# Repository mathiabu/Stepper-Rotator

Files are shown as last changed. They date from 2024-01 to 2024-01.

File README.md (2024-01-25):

# Stepper-Rotator
Rotation machine for recirculating Organ-on-Chip systems. There are currently 2 versions of the machine: (A) with manual tilt adjustment and (B) with servo-motor controlled tilt adjust. As seen in the image of the fully mounted device, it consists of a main body and a changeable rotor that holds the chips. 

Usage instructions (Version A):
1. Mount the rotor and place the plates/chips.
2. Set the desired tilt by loosening, moving, and tightening the wing nuts on the side.
3. Connect the machine to the power supply (9-12 V) and turn it on (at the backside).
4. While the motor is off (after startup) you can adjust the speed between 0 and 2.5 rpm and also change the rotation direction (clockwise (CW) or counterclockwise (CCW)) by turning the knob.
5. To run the motor, press the on/off button. The user input is blocked while the motor is running. If you want to change the speed, turn the motor off, adjust the speed, and run it again.

Mounting instructions of the body (Version A). Please check the attached images if you are unsure how to mount the parts:
1. Laser-cut DXF files into acrylic. Use the following thickness for the different parts: Back, Front, Bottom, and Side: 5 mm, Top: 1.5 mm, Adapter: 6 mm. Use 2x Adapter-left and 2x Side-A. Delete the text and angle scale in Side-A and engrave this in the second step.
2. The sides contain a laser-engravement to display the tilt and on the backside a countersink for the power jack can be engraved. You have to align the engravement with the cut parts and create an overlay to only remove the difference in the software of your lasercutter. All engravements should be 1-2 mm deep.
3. 3D-print the STL files in a hard material using a FDM- or DLP-based printer. Use enough infill to be able to tap a thread later on. Print the mounting cubes 4x each (normal and mirrowed) and the front bar only 1x.
4. Use a drilling machine with a countersink bit to drill countersinks on the outer parts of the sides, the front, and the back.
5. Use a hand-tapping tool with M3 thread to tap threads in all mounting cubes, the front bar, the front, the bottom, and the adapter parts.
6. Mount the Arduino board at the bottom so that the USB port faces the backside using 5mm long distance rolls (motherboard standoffs, or spacers) with M3 thread stack 10 mm distance rolls on top of them to mount the custom-made Arduino shield later on. Mount the power socket and the power switch on the backside. Mount the motor on the top plate using short M3 screws. Screw a long M3 screw to both adapter parts so that the screw head faces inside and the screw sticks out on both sides. Mount the LCD display using 5mm M3 distance rolls, the potentiometer, and the On/off button to the front panel.
7. Mount the adapters to the side parts and loosely fix them with wing nuts. Both adapters should be symmetrically mounted. Mount the motor to the top plate.
8. Solder a red wire from the (+) pole of the connector to the power switch. Solder a red wire (min 15 cm long) to the other pole of the power switch with an open end. Solder a black wire with an open end to the (-) pole of the the power connector (min 15 cm). Solder a 3-pin female connector (pitch 2.54 mm) to the potentiometer and a 2-pin female connector (pitch 2.54 mm) to the on/off button with 15 cm long wires.
9. Mount & solder additional components to the Arduino motorshield and wire as explained in the attached PDF (Wiring-diagramm-A). The orange nets are to be connected to the respective ports at the motor shield. The motor voltage input can be connected using the screw terminal directly from the DC/DC converter. IMPORTANT: Remove the jumper that connects Vin with the motor voltage because you otherwise short-circuit the motor supply voltage.
10. Mount the sides, the front, and the back using the mounting cubes and the front bar. Use the mirrowed and normal versions and rotate them so that the holes fit each other. Set the tilt to 0 degrees and align the top plate (with the mounted motor) with the adapter. Mark the positions for the mounting holes on the adapter and drill 4 holes into the adapter with a diameter of 2.5 mm and a depth of 10mm. Tap a M3 thread into the holes and mount the top plate (with the motor) with 4 screws.
11. Stack the Arduino motor shield and connect the on/off button, the power supply, the potentiometer, the display, and the stepper motor according to the wire diagramm. Check polarity.
12. Finally, close the bottom part and fix it with 4 countersink screws. Connect a USB cable to your computer and flash the firmware (version A) to the Arduino. Disconnect and power with an external power supply. Check if the device is functioning accordingly and mount the rotor using an M2 screw. If the contrast of the LCD screen is too high or too low: Unscrew the front panel and adjust the contrast at the trim potentiometer on the display while the machine is powered. Finally, mount the front panel back.

Mounting instructions (Rotor):
1.  Laser cut the lower part in 1.5 mm and the upper part in 5 mm acrylic (Select the desired version from the folders attached).
2.  3d print the rotor part with an FDM or SLA printer.
3.  Tap an M3 thread in the 4 bigger holes and an M2 thread in the smaller hole that is mounted to the motor shaft.
4.  Drill countersinks in the thinner acrylic part and tap M3 threads in the 5 mm acrylic sheet.
5.  Mount the thinner and the thicker acrylic sheet together with the 3d-printed part using countersink M3 screws.

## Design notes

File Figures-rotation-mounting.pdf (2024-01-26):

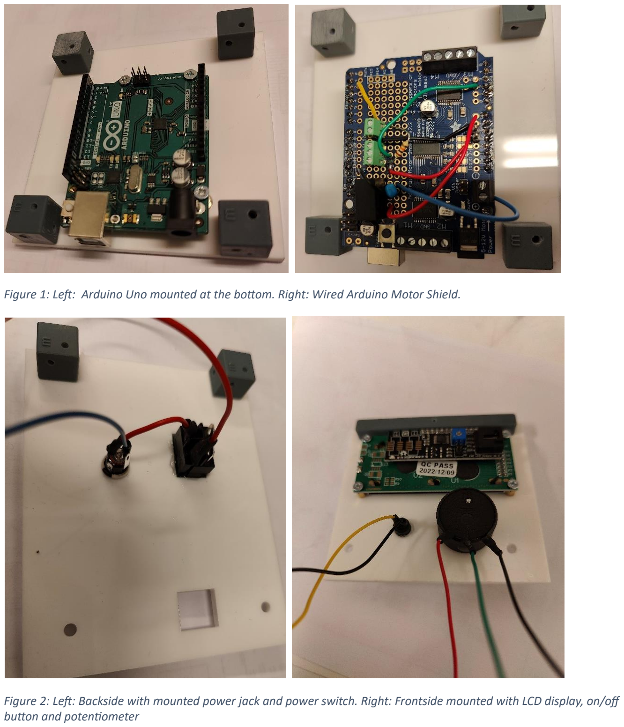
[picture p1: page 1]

Figure 1: Left: Arduino Uno mounted at the bottom. Right: Wired Arduino Motor Shield.

Figure 2: Left: Backside with mounted power jack and power switch. Right: Frontside mounted with LCD display, on/off button and potentiometer

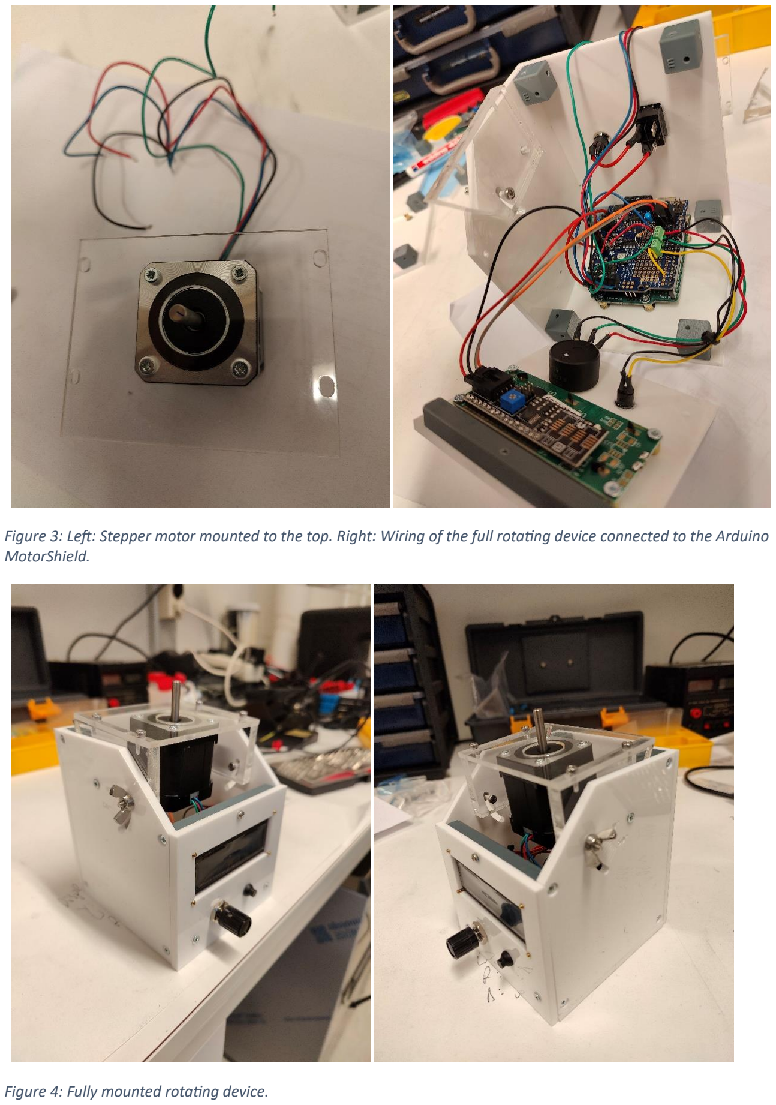
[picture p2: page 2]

Figure 3: Left: Stepper motor mounted to the top. Right: Wiring of the full rotating device connected to the Arduino MotorShield.

Figure 4: Fully mounted rotating device.

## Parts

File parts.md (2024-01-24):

Electrical parts:
- Arduino Uno: https://no.rs-online.com/web/p/arduino/7154081
- LCD display with I2C: https://no.farnell.com/dfrobot/dfr0063/lcd-display-module-i2c-16x2-arduino/dp/3769973
- Stepper motor: https://no.rs-online.com/web/p/stepper-motors/5350401
- Power connector: https://no.rs-online.com/web/p/dc-power-connectors/2596524
- Power supply: https://no.rs-online.com/web/p/ac-dc-adapters/2064915
- Potentiometer: https://no.rs-online.com/web/p/potentiometers/8427002
- Power Switch:
- On/Off button: 
- Motor driver: https://learn.adafruit.com/adafruit-motor-shield-v2-for-arduino/overview
- DC/DC converter for the motor: https://no.rs-online.com/web/p/switching-regulators/1666149
- Jumper wires amd normal wires with different colors.
- 100 uF capacitor, 10 kOhm resistor
- Female connector with 2.54 mm pitch with 2 and 3 pins.

Mechanical parts:
- M3/M2 (countersunk) screws with different length (5-20 mm)
- M3 distance rolls with 5 mm length
- M3 nuts and washers
- Acrylic sheets: 1.5, 5 and 6 mm
- 

Equipment and tools:
- Lasercutter
- FDM or SLA 3d printer
- Soldering iron
- Manual thread making set with M2 and M3 dies
- Screwdriver & wrench (fitting to selected screws)
- Drilling machine with 2.5 mm drilling bit.
- USB-A cable to programm Arduino
- Arduino programming suite

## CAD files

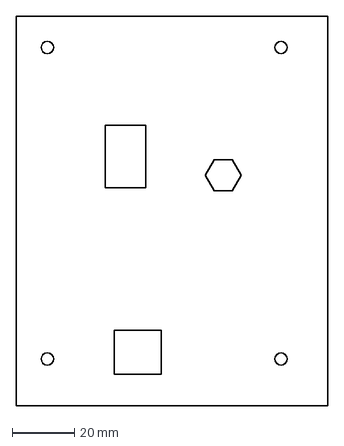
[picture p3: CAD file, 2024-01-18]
cutting-files-rotator/Back-engrave.dxf
100.0 x 125.0 mm

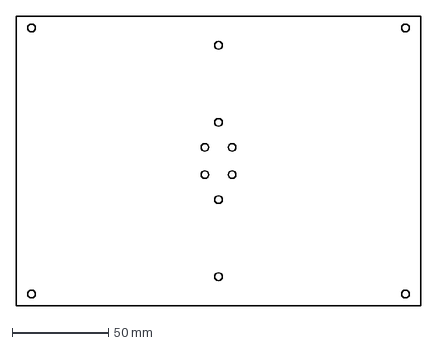
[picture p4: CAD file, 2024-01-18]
cutting-files-rotor/rotor-2-wellplates-btm.dxf
210.0 x 150.0 mm

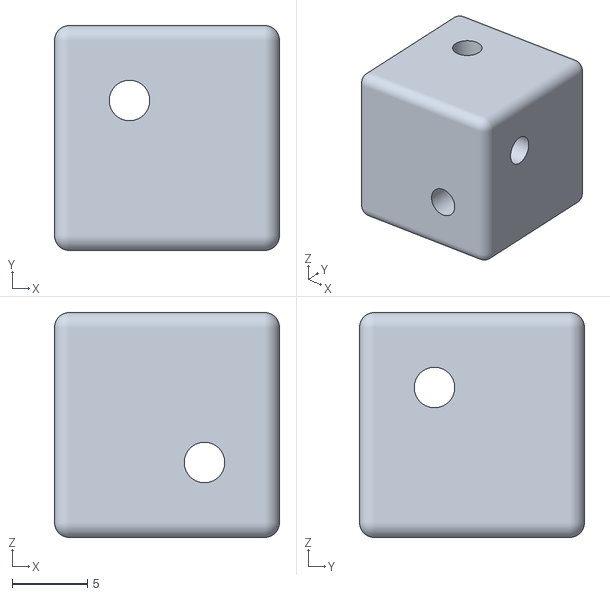
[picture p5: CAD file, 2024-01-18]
STL-rotator/Mounting-Cube-10.stl
15.0 x 15.0 x 15.0

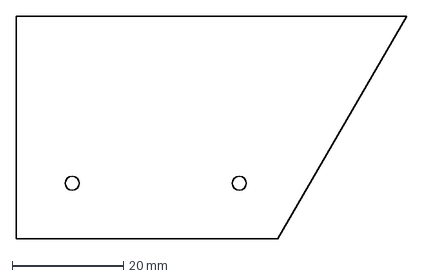
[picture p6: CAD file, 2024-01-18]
cutting-files-rotator/Adapter-left.dxf
70.0 x 40.0 mm

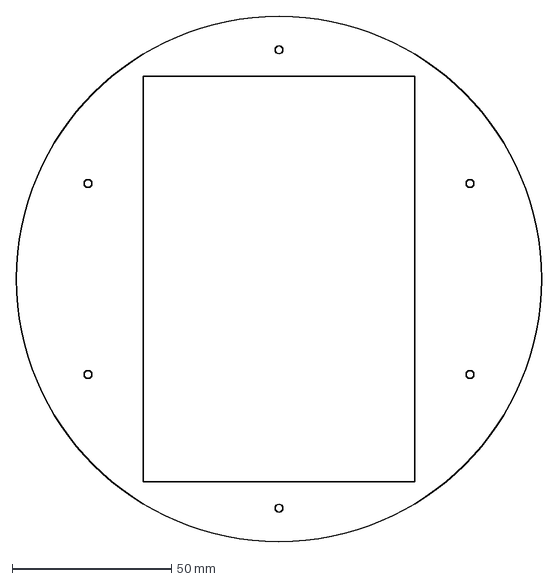
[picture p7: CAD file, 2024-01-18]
cutting-files-rotor/rotor-1-wellplate-top.dxf
165.0 x 165.0 mm

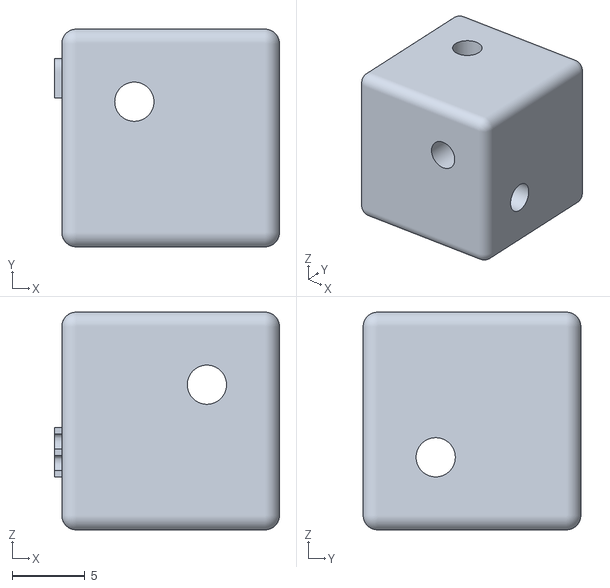
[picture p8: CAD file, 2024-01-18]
STL-rotator/Mounting-Cube-10-mirrow.stl
15.5 x 15.0 x 15.0

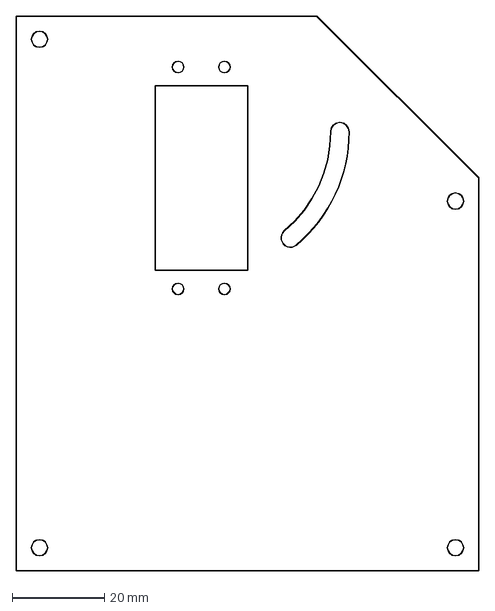
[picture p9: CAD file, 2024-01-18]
cutting-files-rotator/Side-B-right-engrave.dxf
100.0 x 120.0 mm

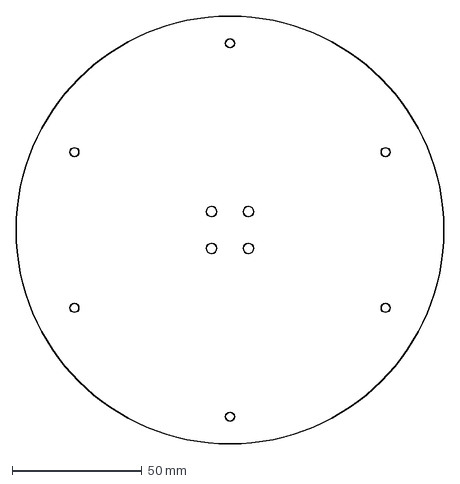
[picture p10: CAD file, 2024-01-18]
cutting-files-rotor/rotor-1-wellplate-btm.dxf
165.0 x 165.0 mm

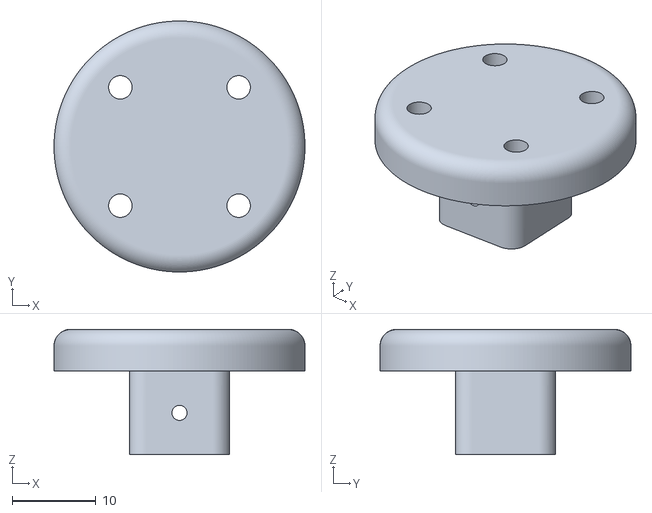
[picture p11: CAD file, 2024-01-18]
STL-rotator/Rotator.stl
30.0 x 30.0 x 15.0

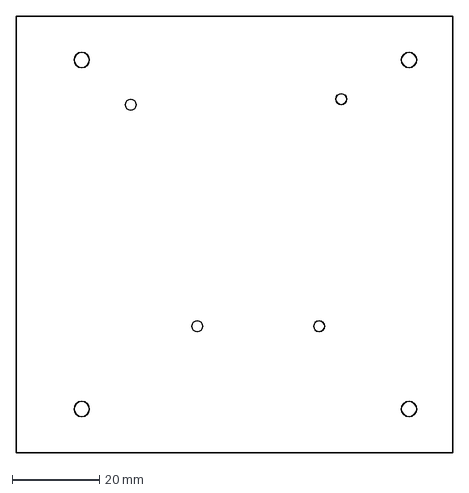
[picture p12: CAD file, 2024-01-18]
cutting-files-rotator/Bottom.dxf
100.0 x 100.0 mm

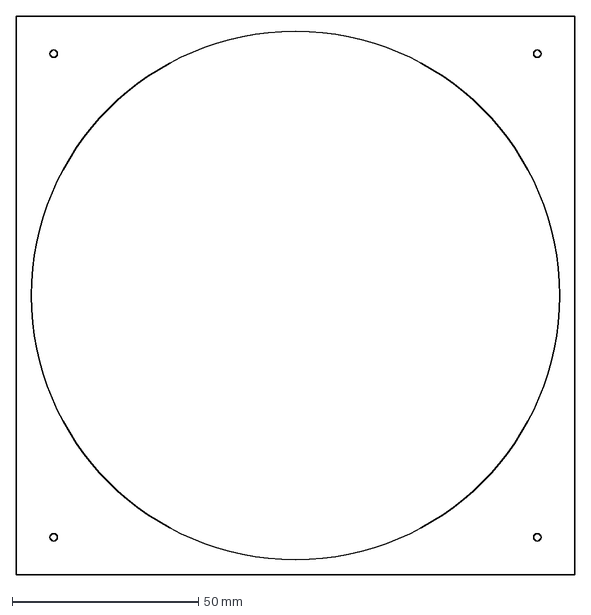
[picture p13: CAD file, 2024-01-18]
cutting-files-rotor/rotor-petri_dish-top.dxf
150.0 x 150.0 mm

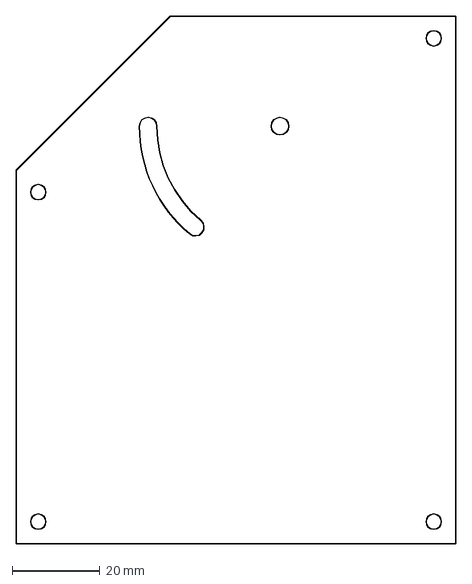
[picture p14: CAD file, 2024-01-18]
cutting-files-rotator/Side-B-left.dxf
100.0 x 120.0 mm

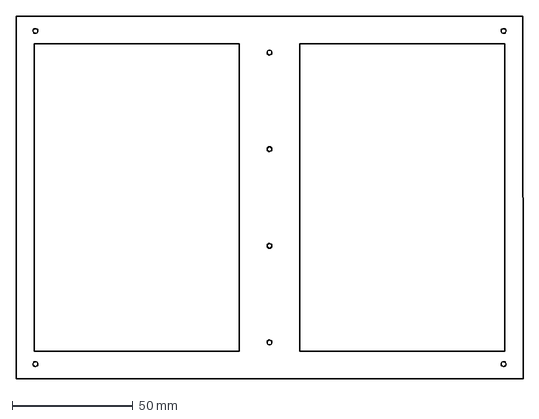
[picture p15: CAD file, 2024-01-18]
cutting-files-rotor/rotor-2-wellplates-top.dxf
210.0 x 150.0 mm

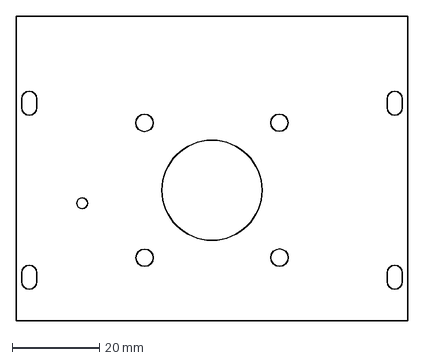
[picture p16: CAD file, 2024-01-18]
cutting-files-rotator/Top.dxf
90.0 x 70.0 mm

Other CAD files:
cutting-files-rotor/rotor-petri_dish-btm.dxf
cutting-files-rotator/Back-cut.dxf
cutting-files-rotator/Adapter-right.dxf
cutting-files-rotator/Side-B-right-cut.dxf
cutting-files-rotator/Front-rotator.dxf
cutting-files-rotator/Side-A.dxf

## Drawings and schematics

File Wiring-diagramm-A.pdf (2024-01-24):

## Free wiring

VCC | VCC | VCC VCC VCC | +5V

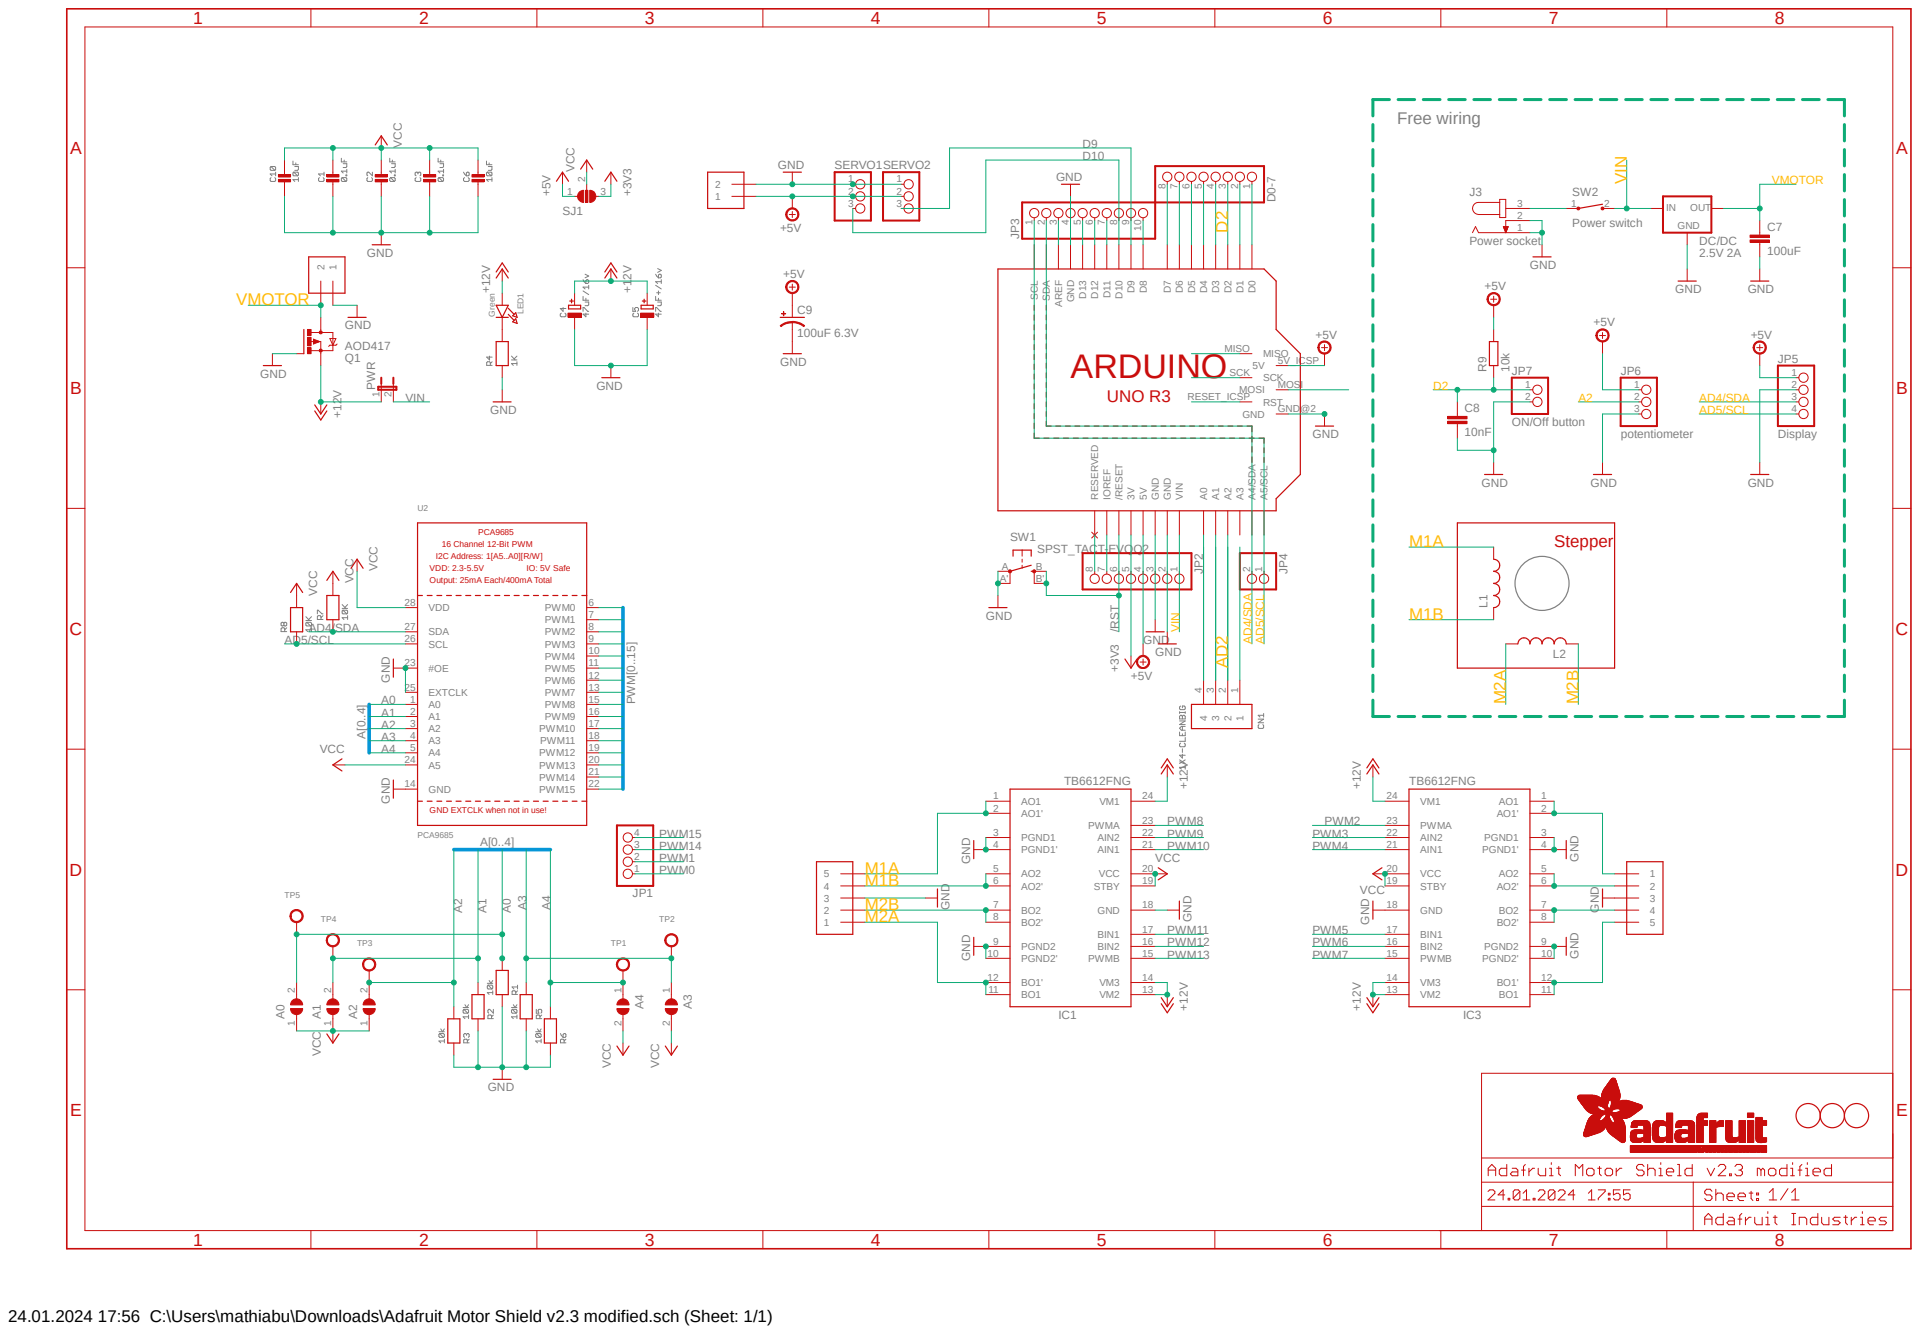
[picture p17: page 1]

5V 5V_ICSP MOSI MOSI GND GND@2 SCK SCK RST RESET_ICSP

24.01.2024 17:56 C:\Users\mathiabu\Downloads\Adafruit Motor Shield v2.3 modified.sch (Sheet: 1/1)

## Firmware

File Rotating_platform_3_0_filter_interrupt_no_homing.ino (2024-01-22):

#include <ezButton.h>
#include <Wire.h>
#include <ServoTimer2.h>
#include <LiquidCrystal_I2C.h>
#include <Adafruit_MotorShield.h>
#include "utility/Adafruit_MS_PWMServoDriver.h"
#include "util/twi.h"
#define STEPS 200
Adafruit_MotorShield AFMS = Adafruit_MotorShield(0x60);
Adafruit_StepperMotor *myMotor;
LiquidCrystal_I2C lcd(0x27, 16, 2);

const int stepperPot = A0;  //controls stepper motor
int sensorpin = 3;          // sensor is attached to Pin 3
int sensorvalue;            //sensor's threshold

ServoTimer2 myServo;          // create servo object to control a servo
const int BUTTON_PIN = 4;     // Arduino pin connected to button's pin
ezButton button(BUTTON_PIN);  // create ezButton object that attach to pin 4;
int lastButtonState;          // the previous state of button
int currentButtonState;       // the current state of button

unsigned long time_0 = 0, time_1 = 0;
int speed_ = 1;
unsigned long period = 10;
int direction_ = 1;
bool state_ = false;
int tilt = 0;
float EMA_a = 0.6;
int EMA_S = 0;
int new_tilt = 0;
volatile int real_tilt = 0;

ISR(TIMER1_COMPA_vect) {
  OCR1A += 50000;  // Advance The COMPA Register handle The Timer Interrupt, 25 ms

  myServo.write(real_tilt);
}

void updatePeriodAndScreen() {
  lcd.setCursor(13, 0);
  if (state_)
    lcd.print("ON ");

  else {
    lcd.print("OFF");
    myMotor->release();
  }

  char msg[16] = "";
  tilt = analogRead(A3);
  EMA_S = (EMA_a * tilt) + ((1 - EMA_a) * EMA_S);


  int new_tilt = map(EMA_S, 0, 1023, 0, 45);  // scales it to use it with the servo (values between 0 and 45)
  lcd.setCursor(0, 1);
  sprintf(msg, "Tilt: %02d", new_tilt);  // printing 09 when angle is below 10
  lcd.print(msg);

  lcd.setCursor(0, 0);  // move cursor to first row, first character
  lcd.print("RPM: ");
  lcd.print((float)abs(speed_) / 100);
  if (speed_ < 0) {
    direction_ = -1;
    lcd.print("CCW");
  } else {
    lcd.print("CW ");
    direction_ = 1;
  }

  int speedValue = analogRead(stepperPot);
  int new_speed = map(speedValue, 0, 1023, -400, 400);  // scale the value of pot to control the rotation speed
  if ((speed_ != new_speed) && (abs(new_speed) > 0))    // if the speed was changed
  {
    speed_ = new_speed;               // set the speed of the motor
    period = 1875 / abs(speed_) - 3;  //time between steps of the motor
  }
}


void updatePeriodAndDirection() {
  int speedValue = analogRead(stepperPot);
  int new_speed = map(speedValue, 0, 1023, -400, 400);
  if ((speed_ != new_speed) && (abs(new_speed) > 0)) {
    speed_ = new_speed;

    period = 1875 / abs(speed_) - 3;

    lcd.setCursor(13, 0);
    if (state_)
      lcd.print("ON ");

    else {
      lcd.print("OFF");
      myMotor->release();
    }

    if (speed_ < 0) {
      direction_ = -1;
    } else {
      direction_ = 1;
    }
  }
}


void runMotor() {
  while (state_) {
    lastButtonState = currentButtonState;
    currentButtonState = digitalRead(4);

    if ((millis() - time_1) >= 1000) {
      updatePeriodAndDirection();
    time_1 = millis();
    }

    if ((millis() - time_0) >= period) {
      if (state_ && (direction_ > 0))
        myMotor->onestep(FORWARD, MICROSTEP);
      else if (state_)
        myMotor->onestep(BACKWARD, MICROSTEP);
      time_0 = millis();
    }

    if (lastButtonState == HIGH && currentButtonState == LOW) {
      state_ = !state_;
      if ((millis() - time_1) >= 1000) {
        updatePeriodAndDirection();
      time_1 = millis();
      }
    }
  }
}


void runMotorFast() {
  while (state_) {
    lastButtonState = currentButtonState;
    currentButtonState = digitalRead(4);
    if ((millis() - time_1) >= 1000) {
      updatePeriodAndDirection();
    time_1 = millis();
    }
    if (state_ && (direction_ > 0))
      myMotor->onestep(FORWARD, MICROSTEP);
    else if (state_)
      myMotor->onestep(BACKWARD, MICROSTEP);

    if (lastButtonState == HIGH && currentButtonState == LOW) {
      state_ = !state_;
      if ((millis() - time_1) >= 1000) {
        updatePeriodAndDirection();
      time_1 = millis();
      }
    }
  }
}


void eightWellsChip() {
  while (state_) {
    if ((millis() - time_1) >= 1000) {
      updatePeriodAndScreen();
      time_1 = millis();
    }

    for (int y = 0; y < 950; y++) {
      lastButtonState = currentButtonState;
      currentButtonState = digitalRead(4);

      if (state_ && (direction_ > 0))
        myMotor->onestep(FORWARD, MICROSTEP);
      else if (state_)
        myMotor->onestep(BACKWARD, MICROSTEP);

      if (lastButtonState == HIGH && currentButtonState == LOW) {
        state_ = !state_;
        if ((millis() - time_1) >= 1000) {
          updatePeriodAndDirection();
        time_1 = millis();
    }
      }
    }

    for (int i = 0; i < 650; i++) {
      lastButtonState = currentButtonState;
      currentButtonState = digitalRead(4);

      if ((millis() - time_0) >= period) {
        if (state_ && (direction_ > 0))
          myMotor->onestep(FORWARD, MICROSTEP);
        else if (state_)
          myMotor->onestep(BACKWARD, MICROSTEP);

        time_0 = millis();
        int speedValue = analogRead(stepperPot);
        int new_speed = map(speedValue, 0, 1023, -400, 400);
        tilt = analogRead(A3);
        EMA_S = (EMA_a * tilt) + ((1 - EMA_a) * EMA_S);


        int new_tilt = map(EMA_S, 0, 1023, 0, 45);  // scales it to use it with the servo (values between 0 and 45)

        if ((millis() - time_1) >= 1000) {
          updatePeriodAndDirection();
        time_1 = millis();
    }
      } else i--;
      if (lastButtonState == HIGH && currentButtonState == LOW) {
        state_ = !state_;
        if ((millis() - time_1) >= 1000) {
          updatePeriodAndDirection();
        time_1 = millis();
    }
      }
    }
  }
}


void homing() {
  myMotor->release();
  lcd.init();
  lcd.backlight();
  lcd.setCursor(0, 0);
  lcd.print("HOMING");
  while (digitalRead(sensorpin) != 0) {
    myMotor->onestep(FORWARD, MICROSTEP);  // rotate the motor by one step
  }
}


void setup() {
  Serial.begin(9600);          // initialize serial
  button.setDebounceTime(90);  // set debounce time to 90 milliseconds
  myServo.attach(9);           // attaches the servo on pin 9 to the servo object
  myServo.write(tilt);         //sets the servo to 0 deg tilt

  Wire.begin();
  Wire.setClock(400000UL);  //High Speed I2C mode, increase the sample rate to 4kHz.

  AFMS.begin();
  myMotor = AFMS.getStepper(STEPS, 1);
  myMotor->setSpeed(1);

  //homing();// setting the platform to the home position;
  myMotor->release();

  lcd.init();
  lcd.backlight();
  lcd.setCursor(13, 0);
  lcd.print("OFF");
  currentButtonState = digitalRead(4);
  EMA_S = analogRead(A3);
  TCCR1A = 0;           // Init Timer1A
  TCCR1B = 0;           // Init Timer1B
  TCCR1B |= B00000010;  // Prescaler = 8
  OCR1A = 50000;        // Timer Compare1A Register
  TIMSK1 |= B00000010;  // Enable Timer COMPA Interrupt
}

void loop() {
  lastButtonState = currentButtonState;
  currentButtonState = digitalRead(4);

  //myServo.write(0); //use this line only in testing mode

  int analogTiltPot = analogRead(A3);
  EMA_S = (EMA_a * analogTiltPot) + ((1 - EMA_a) * EMA_S);
  //new_tilt = map(EMA_S, 0, 1023, 0, 45);  // scales it to use it with the servo (values between 0 and 45)
  real_tilt = map(EMA_S, 0, 1023, 750, 1500);


  if ((millis() - time_1) >= 1000) {
    updatePeriodAndScreen();
    time_1 = millis();
  }


  if (lastButtonState == HIGH && currentButtonState == LOW) {
    state_ = !state_;  // toggle state
    if ((millis() - time_1) >= 1000) {
      updatePeriodAndScreen();
      time_1 = millis();
    }
    //eightWellsChip();
    runMotor();
    //runMotorFast();
  }
}

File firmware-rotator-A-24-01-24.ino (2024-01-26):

#include <Wire.h>
#include <Adafruit_MotorShield.h>
#include "utility\Adafruit_MS_PWMServoDriver.h"
#include <LiquidCrystal_I2C.h>
// Steps for a full rotation with 0.9 deg step angle
#define STEPS 400
// Microstepping divides one step by 16
#define MICROSTEPS 16
// delay in ms for debouncing
#define BUTTON_DELAY 200

// Set motor shield I2C adress to 0x60
Adafruit_MotorShield AFMS = Adafruit_MotorShield(0x60);
Adafruit_StepperMotor *myMotor;

// LCD pins <--> Arduino pins
LiquidCrystal_I2C lcd(0x27, 16, 2);

const int pot    = A2;    //controls stepper motor
const int button = 2;     //linked to an interrupt

unsigned long time_0 = 0;
int speed_ = 1, new_speed = 1;
unsigned long period = 10;
byte direction_ = FORWARD;
volatile bool state_ = false, state_old = false;
volatile unsigned long button_time = 0;

// ISR to change state of the firmware when button is pressed
void toggleMotor() {
  if((millis() - button_time) < BUTTON_DELAY)
    return;
  state_old = state_;
  state_ ^= 1;
  button_time = millis();      
}

void setup() {
  // Set PWM modulation frequency to 4000 Hz
  AFMS.begin(4000);
  // put your setup code here, to run once:
  myMotor = AFMS.getStepper(STEPS/MICROSTEP,2);
  myMotor->setSpeed(1);
  myMotor->release();
  // set the time for button debouncing
  button_time = millis();
  // Initialize digitial input and ISR for button
  pinMode(button, INPUT);
  attachInterrupt(digitalPinToInterrupt(button), toggleMotor, FALLING);
  // Initialize analog input for potentiometer
  pinMode(pot, INPUT);
  analogReference(DEFAULT);
  // Initialize LCD display
  lcd.init();
  lcd.backlight();
  lcd.setCursor(12, 0);
  lcd.print("OFF");
}

void loop() { 
  // Machine is turned on: Motor off and display "off" on display
  if((state_ == false) && (state_old == true)) {
    lcd.setCursor(12, 0);
    lcd.print("OFF ");
    myMotor->release();
    state_old = false;
  }
  // Machine is turned on: Display "on", lock user input and start rotating
  else if((state_ == true) && (state_old == false)) {
    lcd.setCursor(12, 0);
    lcd.print("ON ");
    state_old = true;
  }
  // No change: Read potentiometer and set rotation speed
  else if((state_ == false) && (state_old == false)) {
    // Map reading of input to -2.5 to 2.5 rpm (multiplied by 100)
    new_speed = map(analogRead(pot), 1023, 0, -250, 250);

    if ((speed_ != new_speed) && (abs(new_speed) > 0)) // if the speed was changed
    { 
      speed_ = new_speed;
      // Calculate time between two steps in ms
      period = 6000000/abs(speed_)/STEPS/MICROSTEPS-2;
    
      lcd.setCursor(0, 0);         // move cursor to second row
      lcd.print("Dir: ");
      // Set direction based on polarity: negative: counterclockwise rotation (CCW). positive: clockwise rotation (CW)
      if(speed_ > 0) {
        direction_ = FORWARD;
        lcd.print("CCW");
      }
      else {
        lcd.print("CW ");
        direction_ = BACKWARD;
      }
     
      lcd.setCursor(0, 1);         // move cursor to second row
      lcd.print("Speed: ");
      lcd.print((float) abs(speed_)/100);
      lcd.setCursor(13, 1);
      lcd.print("rpm");
    }
  }
  // If GUI is locked: Check if elapsed time since last step > period between steps and move one step in the selected direction
  else {
    if((millis() - time_0) >= period) {
        myMotor->onestep(direction_, MICROSTEP);
        time_0 = millis();
    }
  }

}
